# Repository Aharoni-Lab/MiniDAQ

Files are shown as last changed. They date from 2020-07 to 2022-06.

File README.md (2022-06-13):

# MiniDAQ
Simplified DAQ for Miniscopes and Minicams. This is effectively a smaller version of the [standard Miniscope DAQ](https://github.com/daharoni/Miniscope_DAQ_PCB) and does not include easily accessible trigger and sync connections but should support all other functionality of the Miniscope platform.

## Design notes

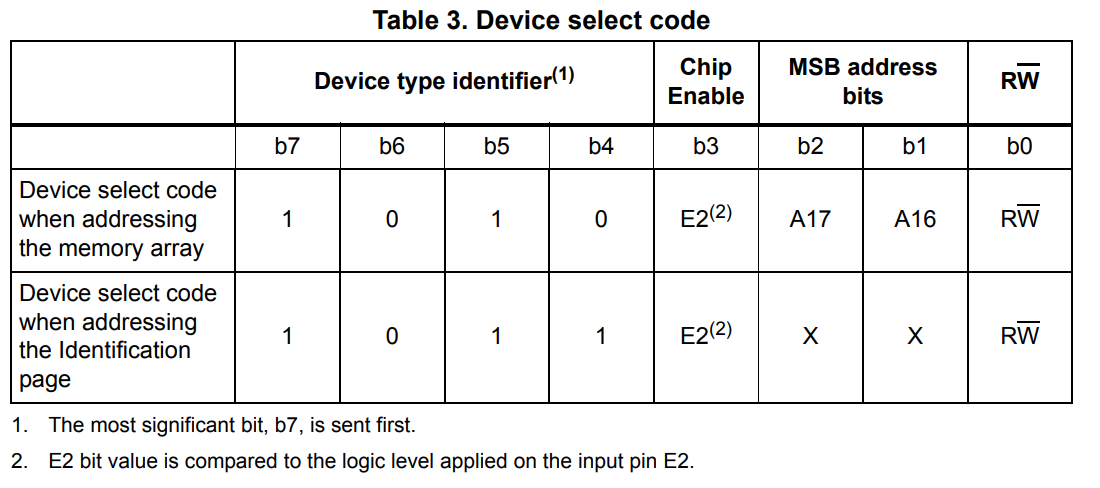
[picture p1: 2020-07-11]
KiCad/img/M24M02_I2C_ADDR.PNG

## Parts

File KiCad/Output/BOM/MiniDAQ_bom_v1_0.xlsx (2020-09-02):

Component | Description | Part | References | Value | Footprint | Quantity Per PCB | Datasheet | Part Number | Note | Size
1 | Unpolarized capacitor, small symbol | C_Small | C79 | 0 Res | C_0201_0603Metric_L | 1 | ~ | ERJ-1GN0R00C
2 | Unpolarized capacitor, small symbol | C_Small | C2 C5 C7 C10 C12 C15 C20 C23 C26 C30 C35 C37 C39 C40 C41 C43 C45 C46 C48 C50 C51 C53 C57 C58 C59 C61 C63 C65 C67 C68 C70 C72 C74 | 0.1uF | C_0201_0603Metric_L | 33 | ~ | CC0201KRX5R6BB104
3 | Unpolarized capacitor, small symbol | C_Small | C1 C6 C9 C13 C14 C18 C19 C24 C25 C29 C38 C42 C49 C54 C60 C64 C66 C69 C71 | 10nF | C_0201_0603Metric_L | 19 | ~ | CC0201KRX7R7BB103
4 | Unpolarized capacitor, small symbol | C_Small | C4 C22 C28 C32 C73 C75 | 10uF | C_0402_1005Metric_L | 6 | ~ | CC0402MRX5R5BB106
5 | Unpolarized capacitor, small symbol | C_Small | C55 C56 | 12pF | C_0201_0603Metric_L | 2 | ~ | CC0201JRNPO8BN120
6 | Unpolarized capacitor, small symbol | C_Small | C16 C21 C27 C31 C33 C34 C77 C78 | 1uF | C_0201_0603Metric_L | 8 | ~ | CC0201MRX5R5BB105
7 | Unpolarized capacitor, small symbol | C_Small | C36 C47 C52 | 2.2uF | C_0402_1005Metric_L | 3 | ~ | CC0402MRX5R6BB225
8 | Unpolarized capacitor, small symbol | C_Small | C44 C62 C76 | 22uF | C_0402_1005Metric_L | 3 | ~ | CL05A226MQ5N6J8
9 | Unpolarized capacitor, small symbol | C_Small | C3 C8 C11 | 4.7uF | C_0402_1005Metric_L | 3 | ~ | CC0402MRX5R6BB475
10 | Unpolarized capacitor, small symbol | C_Small | C17 | 47nF | C_0201_0603Metric_L | 1 | ~ | CC0201KRX5R5BB473
11 | Dual LED, cathodes on pins 3 and 4 | LTST-C155GEKT | D1 | LTST-C155GEKT | LED_4_P138_270X320X110L50X90N | 1 | https://media.digikey.com/pdf/Data%20Sheets/Lite-On%20PDFs/LTST-C155GEKT.pdf | LTST-C155GEKT
15 | USB 3.0 A connector | USB3_A | J1 | USB3_A | USB3_A_Plug_Wuerth_692112030100_Horizontal | 1 | ~ | 692112030100
16 | Edge mount SMA | SMA | J2 | SMA-J-P-H-ST-EM1 |  | 1 |  | SMA-J-P-H-ST-EM1
17 | FIXED IND 47UH 500MA 900 MOHM | ADL3225V-470MT-TL000 | L11 | ADL3225V-470MT-TL000 | L_1210_3225Metric_L | 1 | https://product.tdk.com/info/en/catalog/datasheets/inductor_automotive_decoupling_adl3225v_en.pdf | ADL3225V-470MT-TL000 | 47uH | 1210
18 | FERRITE BEAD 470 OHM 0603 1LN | BLM18PG471SN1D | L1 L2 L3 L5 L6 L8 L9 L10 | BLM18PG471SN1D | L_0603_1608Metric_L | 8 | https://www.murata.com/en-us/products/productdata/8796738650142/ENFA0003.pdf | BLM18PG471SN1D | 470 Ohms @ 100MHz | 603
19 | Inductor, small symbol | L_Small | L4 L7 | BLM21PG221SN1D | L_0805_2012Metric | 2 | https://www.murata.com/en-us/products/en-us/products/productdata/8796738977822/ENFA0005.pdf | BLM21PG221SN1D
20 | Inductor, small symbol | L_Small | L12 | LQM2HPN1R0MG0 | L_1008_2520Metric_L | 1 | https://www.mouser.com/datasheet/2/281/JELF243B-0019-1634195.pdf | LQM2HPN1R0MG0
21 | TRANS NPN 40V 0.2A DFN1006-3 | MMBT3904LP-7B | Q1 Q2 | MMBT3904LP-7B | TRXDFN3_101X61X53L25X15N | 2 | https://www.diodes.com/assets/Datasheets/ds31835.pdf | MMBT3904LP-7B
22 | Resistor, small US symbol | R_Small_US | R41 R42 | 0 | R_0201_0603Metric_ERJ_L | 2 | ~ | ERJ-1GN0R00C
23 | Resistor, small US symbol | R_Small_US | R5 R8 | 0 1% | R_0201_0603Metric_ERJ_L | 2 | ~ | ERJ-1GN0R00C
24 | Resistor, small US symbol | R_Small_US | R1 R2 R3 R9 R14 R15 R29 R43 | 10K | R_0201_0603Metric_ERJ_L | 8 | ~ | ERJ-1GNF1002C
25 | Resistor, small US symbol | R_Small_US | R4 R6 | 10K 1% | R_0201_0603Metric_ERJ_L | 2 | ~ | ERJ-1GNF1002C
26 | Resistor, small US symbol | R_Small_US | R12 | 200 1% | R_0201_0603Metric_ERJ_L | 1 | ~ | ERJ-1GEF2000C
27 | Resistor, small US symbol | R_Small_US | R16 R17 R18 R19 R20 R21 R22 R23 R26 R27 R28 R33 R34 R35 R36 R37 R38 R39 R40 | 22 | R_0201_0603Metric_ERJ_L | 19 | ~ | ERJ-1GNF22R0C
28 | Resistor, small US symbol | R_Small_US | R10 R11 R24 R25 R30 R31 R32 | 2k | R_0201_0603Metric_ERJ_L | 7 | ~ | ERJ-1GNF2001C
29 | Resistor, small US symbol | R_Small_US | R7 | 50 | R_0201_0603Metric_ERJ_L | 1 | ~ | ERJ-1GNF49R9C
30 | Resistor, small US symbol | R_Small_US | R13 | 6.04K 1% | R_0201_0603Metric_ERJ_L | 1 | ~ | ERJ-1GNF6041C
31 | EZ-USBÂ® FX3:SuperSpeed USB Controller | CYUSB3014 | U4 | CYUSB3014 | BGA121CP80_11X11_1000X1000X120B30 | 1 | https://www.cypress.com/file/140296/download | CYUSB3014-BZXC
32 | IC DESERIALIZER 12 BIT 48-VQFN | DS90UB934-Q1 | U1 | DS90UB934-Q1 | QFN_49_P50_700X700X100L40X24T410N | 1 | http://www.ti.com/lit/ds/symlink/ds90ub934-q1.pdf | DS90UB914ATRHSJQ1
33 | 2-Mbit serial IÂ²C bus EEPROM | M24M02-R | U5 | M24M02-R | M24M02-R | 1 | https://www.st.com/content/ccc/resource/technical/document/datasheet/b7/de/9b/f6/03/28/4e/8e/CD00290537.pdf/files/CD00290537.pdf/jcr:content/translations/en.C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 | M24M02-DRCS6TP/K
34 | USB Positive Overvoltage | NCP360 | U2 | NCP360 | SON7P65_200X200X55L30X30T160X90L | 1 | https://www.onsemi.com/pub/Collateral/NCP360-D.PDF | NCP360MUTBG
35 |  | NCP690MN50T2G(5V) | U7 | NCP692MN18T2G | NCP692MN50T2G | 1 | https://www.onsemi.com/pub/Collateral/NCP690-D.PDF | NCP692MN18T2G
36 | 2.5MHz, 1.5A Synchronous Step Down Regulator | SC189xULTRT | U6 | SC189CULTRT | SON_7P50_200X200X57L35X24T170X80N | 1 | https://www.mouser.com/datasheet/2/761/sc189-1366204.pdf | SC189CULTRT
37 | TVS Diode Array | SP3010-04UTG | U3 | SP3010-04UTG | uDFN-10 | 1 | https://www.littelfuse.com/~/media/electronics/datasheets/tvs_diode_arrays/littelfuse_tvs_diode_array_sp3010_datasheet.pdf.pdf | SP3010-04UTG
38 | 2.5mm x 2mm | SMD_CRYSTAL | Y1 | SMD_CRYSTAL | Crystal_SMD_2016-4Pin_2.0x1.6mm | 1 |  | CX2016DB19200H0FLJC2
Component Groups: | 38
Component Count: | 153
Fitted Components: | 153
Number of PCBs: | 1
Total components: | 153
Schematic Version: | v1.0
Schematic Date: | 2020-09-01
PCB Variant: | [u'default']
BoM Date: | 2020-07-15
Schematic Source: | C:\Users\DBAharoni\Documents\Projects\MiniDAQ\KiCad\MiniDAQ.sch
KiCad Version: | Eeschema (5.1.5)-3

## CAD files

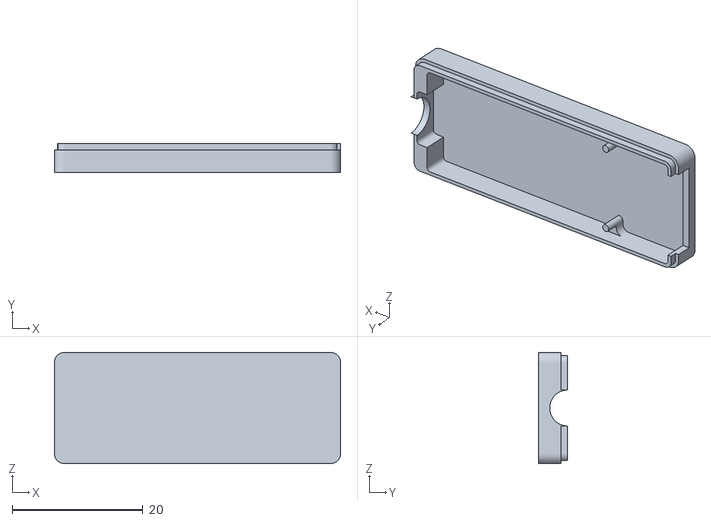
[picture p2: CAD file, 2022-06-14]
MiniDAQ-Body-Parts/MiniDAQ_Shell_Bottom.stl
43.8 x 4.50 x 17.0

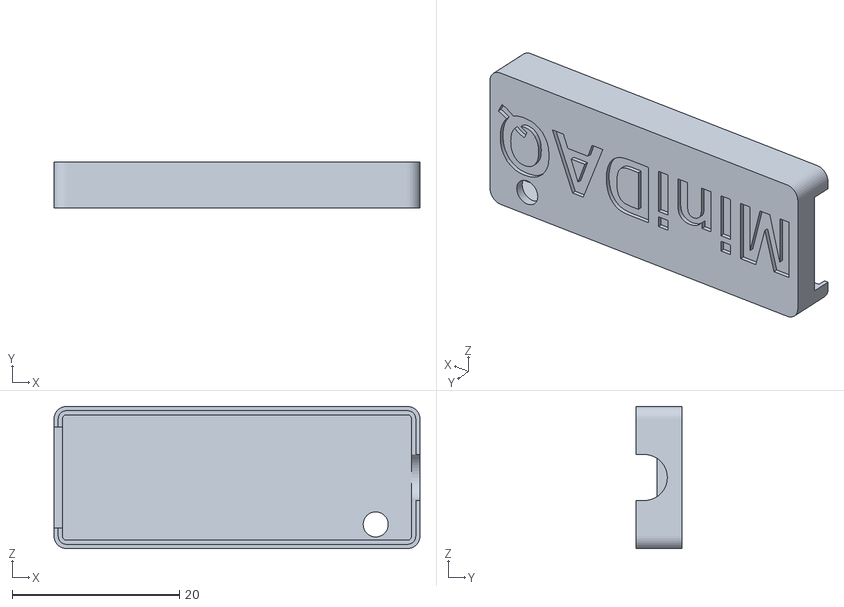
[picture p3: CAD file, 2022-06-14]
MiniDAQ-Body-Parts/MiniDAQ_Shell_Top.stl
43.8 x 5.50 x 17.0

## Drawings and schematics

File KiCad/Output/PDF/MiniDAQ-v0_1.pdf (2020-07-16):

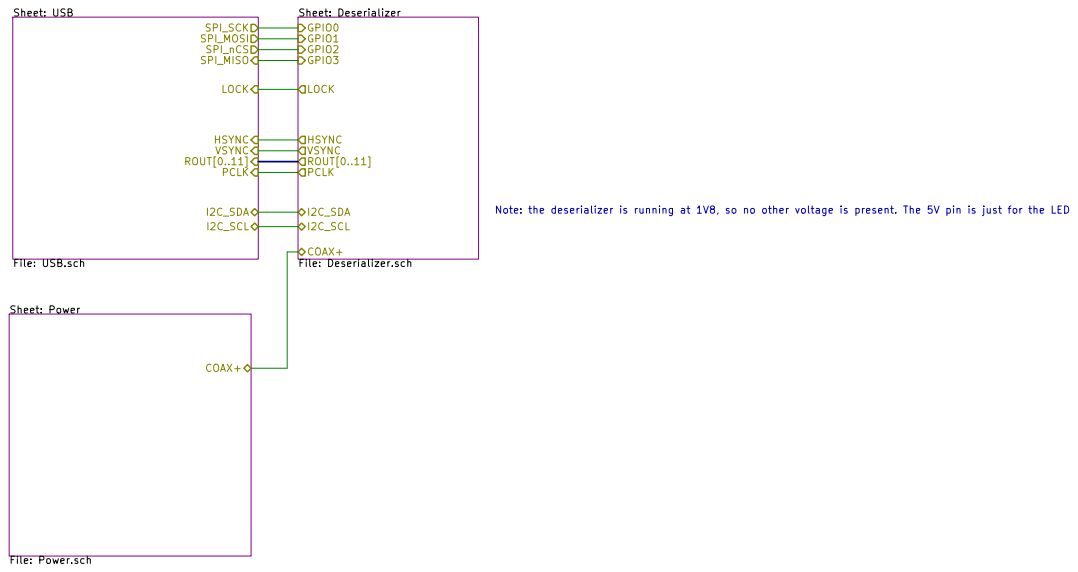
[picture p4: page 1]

File: MiniDAQ.sch Sheet: / Daniel Aharoni

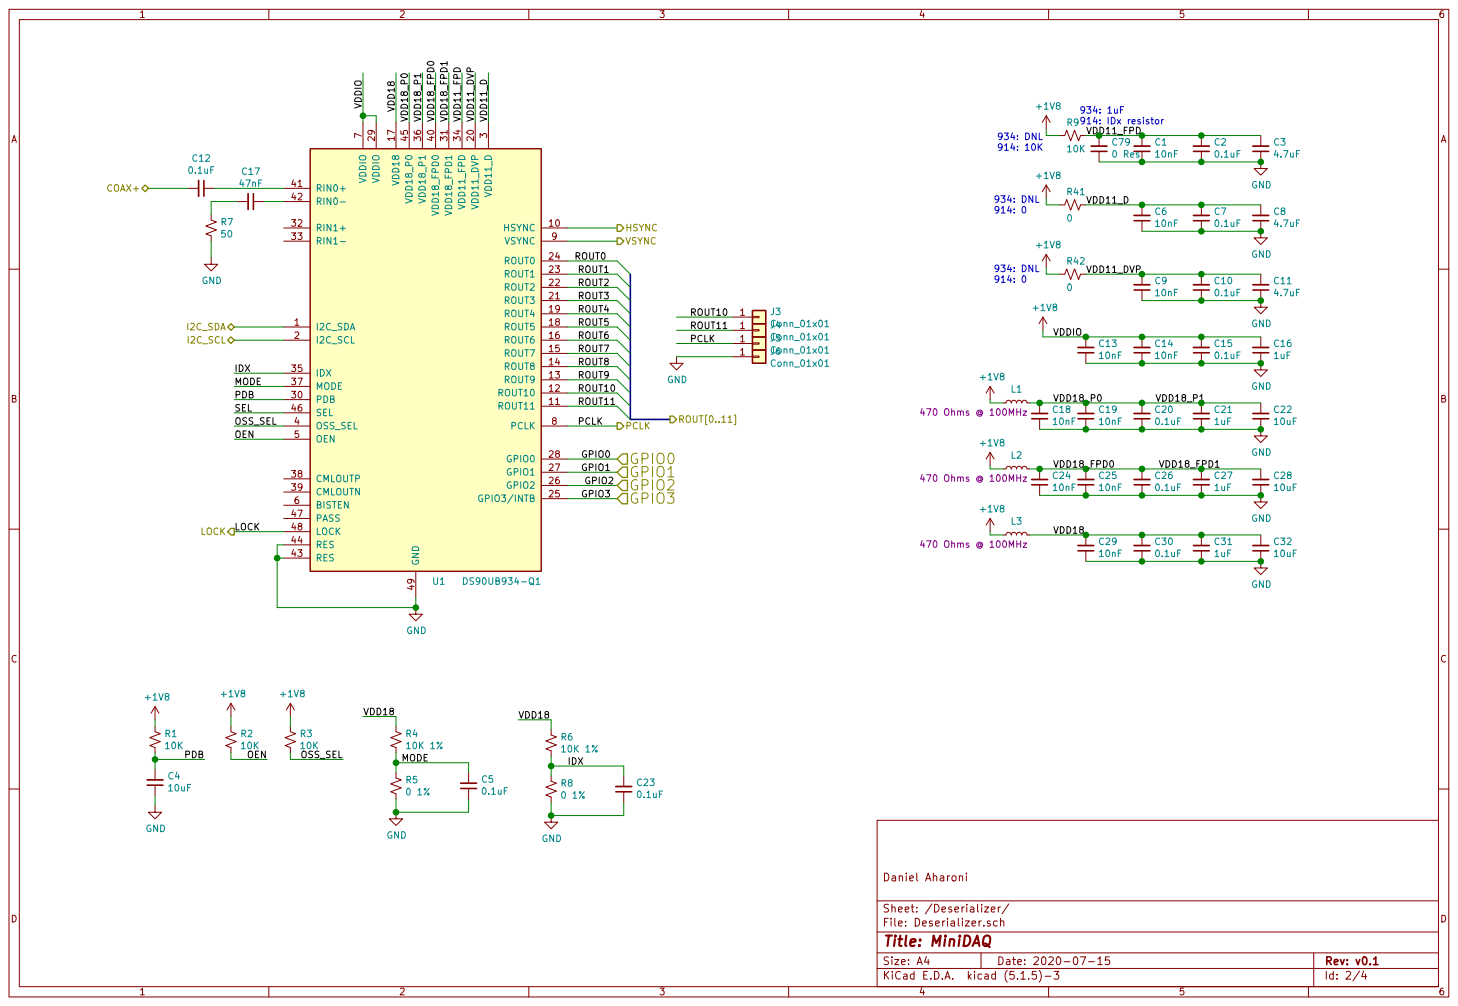
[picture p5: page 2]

File: Deserializer.sch Sheet: /Deserializer/ Daniel Aharoni GND

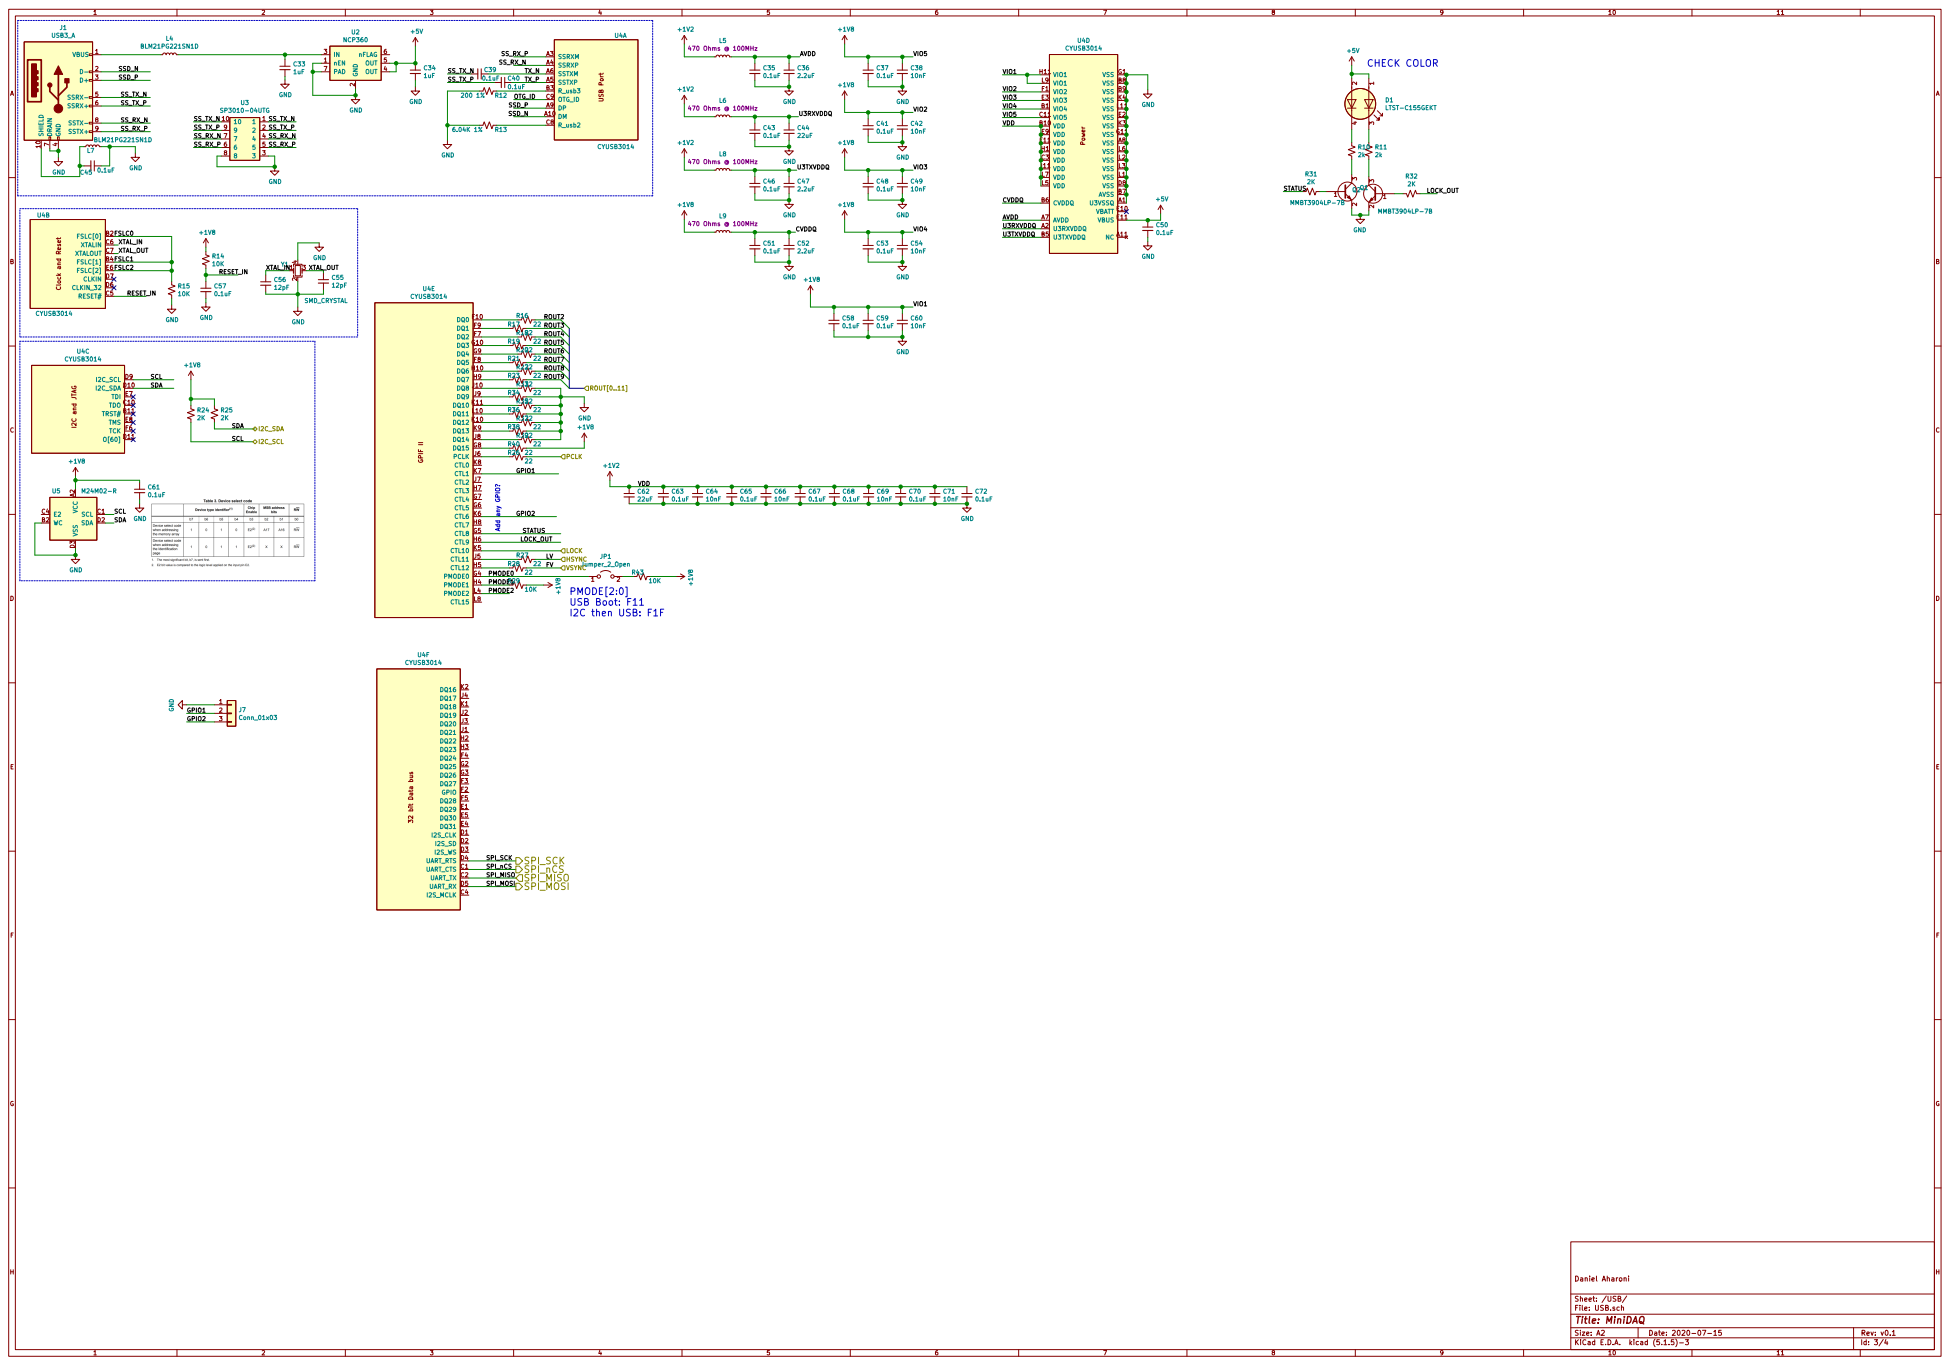
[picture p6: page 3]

File: USB.sch Sheet: /USB/ Daniel Aharoni

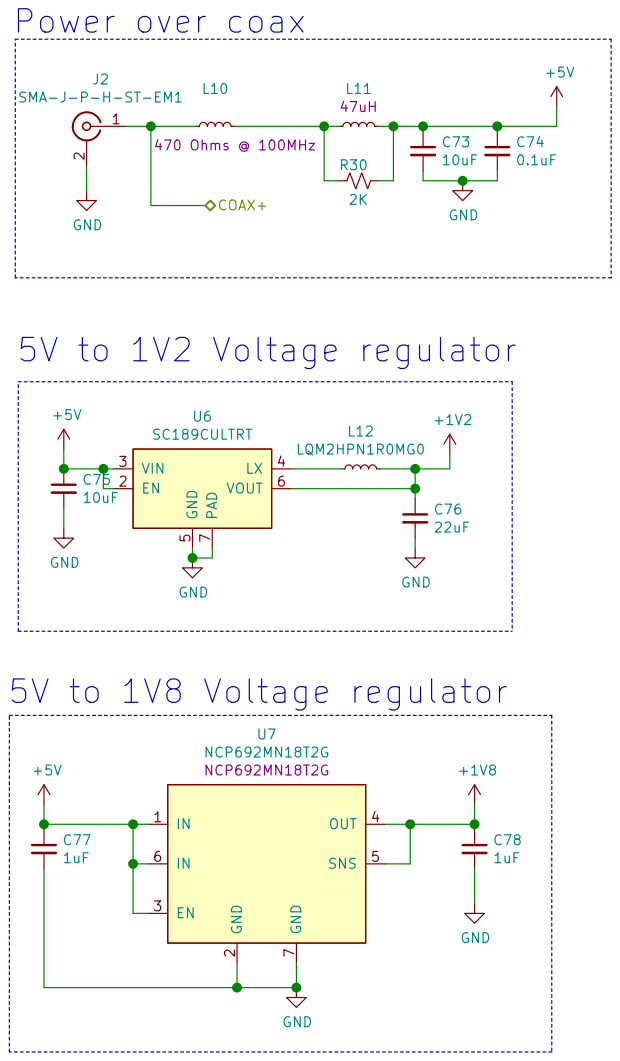
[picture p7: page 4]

2K COAX+ 5V to 1V8 Voltage regulator

File: Power.sch Sheet: /Power/ Daniel Aharoni

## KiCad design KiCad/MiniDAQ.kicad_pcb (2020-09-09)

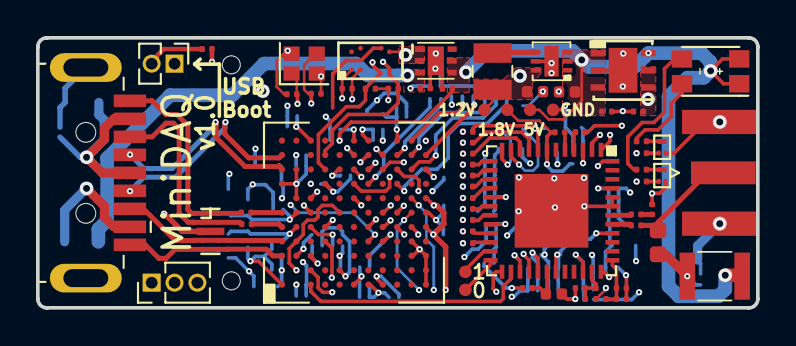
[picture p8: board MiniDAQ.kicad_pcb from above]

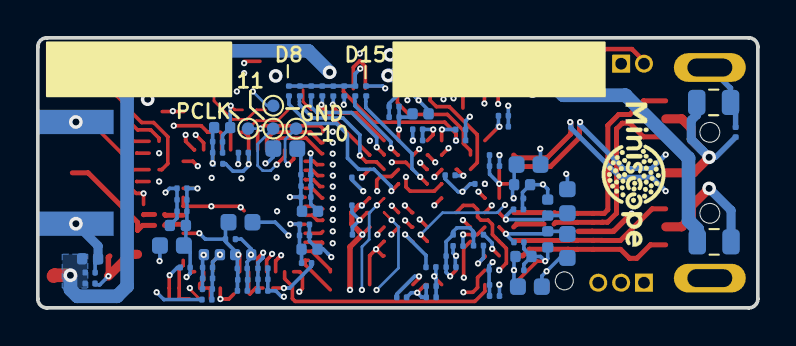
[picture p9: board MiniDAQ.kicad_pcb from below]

Board: 6 copper layers, 40.0 x 15.0 mm, 161 parts (93 on the bottom side), 96 nets.

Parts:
C1, C6, C9, C13, C14, C18, C19, C24, C25, C29, C38, C42, C49, C54, C60, C64, C66, C69, C71: 10nF; C_0201_0603Metric_L
C2, C5, C7, C10, C12, C15, C20, C23, C26, C30, C35, C37, C39, C40, C41, C43, C45, C46, C48, C50, C51, C53, C57, C58, C59, C61, C63, C65, C67, C68, C70, C72, C74: 0.1uF; C_0201_0603Metric_L
C3, C8, C11: 4.7uF; C_0402_1005Metric_L
C4, C22, C28, C32, C73, C75: 10uF; C_0402_1005Metric_L
C16, C21, C27, C31, C33, C34, C77, C78: 1uF; C_0201_0603Metric_L
C17: 47nF; C_0201_0603Metric_L
C36, C47, C52: 2.2uF; C_0402_1005Metric_L
C44, C62, C76: 22uF; C_0402_1005Metric_L
C55, C56: 12pF; C_0201_0603Metric_L
C79: 0 Res; C_0201_0603Metric_L
D1: LTST-C155GEKT; LED_4_P138_270X320X110L50X90N
J1: USB3_A; USB3_A_Plug_Wuerth_692112030100_Horizontal
J2: SMA-J-P-H-ST-EM1; SMA_Samtec_SMA-J-P-H-ST-EM1_EdgeMount
J3, J4, J5, J6: Conn_01x01; Conn_1x1_700_Circular_Pad
J7: Conn_01x03; PinHeader_1x03_P1.27mm_Vertical
JP1: Jumper_2_Open; PinHeader_1x02_P1.27mm_Vertical
J_NA: Conn_01x01; Conn_1x1_700_Circular_Pad
J_NA#2, J_NA#3, J_NA#4, J_NA#5, J_NA#6, J_NA#7, J_NA#8: Conn_01x01; Conn_1x1_700_Circular_Pad
L1, L2, L3, L5, L6, L8, L9, L10: BLM18PG471SN1D; L_0603_1608Metric_L
L4, L7: BLM21PG221SN1D; L_0805_2012Metric
L11: ADL3225V-470MT-TL000; L_1210_3225Metric_L
L12: LQM2HPN1R0MG0; L_1008_2520Metric_L
Q1, Q2: MMBT3904LP-7B; TRXDFN3_101X61X53L25X15N
R1, R2, R3, R9, R14, R15, R29, R43: 10K; R_0201_0603Metric_ERJ_L
R4, R6: 10K 1%; R_0201_0603Metric_ERJ_L
R5, R8: 0 1%; R_0201_0603Metric_ERJ_L
R7: 50; R_0201_0603Metric_ERJ_L
R10, R11: 2k; R_0201_0603Metric_ERJ_L
R12: 200 1%; R_0201_0603Metric_ERJ_L
R13: 6.04K 1%; R_0201_0603Metric_ERJ_L
R16, R17, R18, R19, R20, R21, R22, R23, R26, R27, R28, R33, R34, R35, R36, R37, R38, R39, R40: 22; R_0201_0603Metric_ERJ_L
R24, R25, R30, R31, R32: 2K; R_0201_0603Metric_ERJ_L
R41, R42: 0; R_0201_0603Metric_ERJ_L
U1: DS90UB934-Q1; QFN_49_P50_700X700X100L40X24T410N
U2: NCP360; SON7P65_200X200X55L30X30T160X90L
U3: SP3010-04UTG; uDFN-10
U4: CYUSB3014; BGA121CP80_11X11_1000X1000X120B30
U5: M24M02-R
U6: SC189CULTRT; SON_7P50_200X200X57L35X24T170X80N
U7: NCP692MN18T2G; NCP692MN50T2G
Y1: SMD_CRYSTAL; Crystal_SMD_2016-4Pin_2.0x1.6mm

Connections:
+1V2: C62.1, C63.1, C64.1, C65.1, C66.1, C67.1, C68.1, C69.1, C70.1, C71.1, C72.1, C76.1, J_NA#6.1, L5.1, L6.1, L8.1, L12.2, U4.B10, U4.C3, U4.E9, U4.F11, U4.H1, U4.J11, U4.L5, U4.L7, U6.6
+1V8: C13.2, C14.2, C15.2, C16.2, C37.1, C38.1, C41.1, C42.1, C48.1, C49.1, C53.1, C54.1, C58.1, C59.1, C60.1, C61.1, C78.1, J_NA#5.1, L1.1, L2.1, L3.1, L9.1, R1.1, R2.1, R3.1, R9.2, R14.1, R24.1, R25.1, R29.1, R40.1, R41.2, R42.2, R43.1, U1.7, U1.29, U4.B1, U4.C11, U4.E3, U4.F1, U4.H11, U4.L9, U5.A2, U7.4, U7.5
+5V: C34.1, C50.1, C73.1, C74.1, C75.1, C77.1, D1.1, D1.2, J_NA#3.1, L11.2, R30.2, U2.4, U2.5, U4.E11, U6.2, U6.3, U7.1, U7.3, U7.6
/Deserializer/COAX+: C12.2, J2.1, L10.1
/Deserializer/GPIO0: U1.28, U4.D4
/Deserializer/GPIO1: U1.27, U4.D5
/Deserializer/GPIO2: U1.26, U4.C1
/Deserializer/GPIO3: U1.25, U4.C2
/Deserializer/HSYNC: R27.1, U1.10
/Deserializer/I2C_SCL: R24.2, U1.2, U4.D9, U5.C1
/Deserializer/I2C_SDA: R25.2, U1.1, U4.D10, U5.D2
/Deserializer/IDX: C23.2, R6.2, R8.1, U1.35
/Deserializer/LOCK: U1.48, U4.K5
/Deserializer/MODE: C5.2, R4.2, R5.1, U1.37
/Deserializer/OEN: R2.2, U1.5
/Deserializer/OSS_SEL: R3.2, U1.4
/Deserializer/PCLK: J5.1, R26.1, U1.8
/Deserializer/PDB: C4.2, R1.2, U1.30
/Deserializer/ROUT0: J_NA#7.1, U1.24
/Deserializer/ROUT1: J_NA#8.1, U1.23
/Deserializer/ROUT2: R16.1, U1.22
/Deserializer/ROUT3: R17.1, U1.21
/Deserializer/ROUT4: R18.1, U1.19
/Deserializer/ROUT5: R19.1, U1.18
/Deserializer/ROUT6: R20.1, U1.16
/Deserializer/ROUT7: R21.1, U1.15
/Deserializer/ROUT8: R22.1, U1.14
/Deserializer/ROUT9: R23.1, U1.13
/Deserializer/ROUT10: J3.1, U1.12
/Deserializer/ROUT11: J4.1, U1.11
/Deserializer/VDD11_D: C6.2, C7.2, C8.2, R41.1, U1.3
/Deserializer/VDD11_DVP: C9.2, C10.2, C11.2, R42.1, U1.20
/Deserializer/VDD11_FPD: C1.2, C2.2, C3.2, C79.2, R9.1, U1.34
/Deserializer/VDD18: C29.2, C30.2, C31.2, C32.2, L3.2, R4.1, R6.1, U1.17
/Deserializer/VDD18_FPD0: C24.2, C25.2, C26.2, C27.2, C28.2, L2.2, U1.31, U1.40
/Deserializer/VDD18_P0: C18.2, C19.2, C20.2, C21.2, C22.2, L1.2, U1.36, U1.45
/Deserializer/VSYNC: R28.1, U1.9
/USB/AVDD: C35.1, C36.1, L5.2, U4.A7
/USB/CVDDQ: C51.1, C52.1, L9.2, U4.B6
/USB/FSLC0: R15.1, U4.B2, U4.B4, U4.E6
/USB/GPIO1: J7.2, U4.K7
/USB/GPIO2: J7.3, U4.K6
/USB/LOCK_OUT: R32.2, U4.H6
/USB/PMODE0: JP1.1, U4.G4
/USB/PMODE1: R29.2, U4.H4
/USB/RESET_IN: C57.1, R14.2, U4.C5
/USB/SSD_N: J1.2, U4.A10
/USB/SSD_P: J1.3, U4.A9
/USB/SS_RX_N: J1.8, U3.4, U3.7, U4.A4
/USB/SS_RX_P: J1.9, U3.5, U3.6, U4.A3
/USB/SS_TX_N: C39.2, J1.5, U3.1, U3.10
/USB/SS_TX_P: C40.2, J1.6, U3.2, U3.9
/USB/STATUS: R31.2, U4.G5
/USB/TX_N: C39.1, U4.A6
/USB/TX_P: C40.1, U4.A5
/USB/U3RXVDDQ: C43.1, C44.1, L6.2, U4.A2
/USB/U3TXVDDQ: C46.1, C47.1, L8.2, U4.B5
/USB/XTAL_IN: C56.1, U4.C6, Y1.1
/USB/XTAL_OUT: C55.1, U4.C7, Y1.3
GND: C1.1, C2.1, C3.1, C4.1, C5.1, C6.1, C7.1, C8.1, C9.1, C10.1, C11.1, C13.1, C14.1, C15.1, C16.1, C18.1, C19.1, C20.1, C21.1, C22.1, C23.1, C24.1, C25.1, C26.1, C27.1, C28.1, C29.1, C30.1, C31.1, C32.1, C33.2, C34.2, C35.2, C36.2, C37.2, C38.2, C41.2, C42.2, C43.2, C44.2, C45.1, C46.2, C47.2, C48.2, C49.2, C50.2, C51.2, C52.2, C53.2, C54.2, C55.2, C56.2, C57.2, C58.2, C59.2, C60.2, C61.2, C62.2, C63.2, C64.2, C65.2, C66.2, C67.2, C68.2, C69.2, C70.2, C71.2, C72.2, C73.2, C74.2, C75.2, C76.2, C77.2, C78.2, C79.1, J1.4, J1.7, J2.2, J6.1, J7.1, J_NA#4.1, L7.2, Q1.2, Q2.2, R5.2, R7.2, R8.2, R12.2, R13.2, R15.2, R33.1, R34.1, R35.1, R36.1, R37.1, R38.1, R39.1, U1.43, U1.44, U1.49, U2.1, U2.2, U2.7, U3.3, U3.8, U4.A1, U4.A8, U4.B7, U4.B8, U4.B9, U4.D8, U4.E2, U4.G1, U4.G11, U4.K3, U4.K4, U4.L1, U4.L2, U4.L3, U4.L6, U4.L11, U5.B2, U5.D3, U6.5, U6.7, U7.2, U7.7, Y1.2, Y1.4
unnamed: C12.1, U1.41
unnamed: C17.1, U1.42
unnamed: C17.2, R7.1
unnamed: C33.1, L4.2, U2.3
unnamed: C45.2, J1.10, L7.1
unnamed: D1.3, R11.1
unnamed: D1.4, R10.1
unnamed: J1.1, L4.1
unnamed: JP1.2, R43.2
unnamed: L10.2, L11.1, R30.1
unnamed: L12.1, U6.4
unnamed: Q1.1, R31.1
unnamed: Q1.3, R10.2
unnamed: Q2.1, R32.1
unnamed: Q2.3, R11.2
unnamed: R12.1, U4.B3
unnamed: R13.1, U4.C8
unnamed: R16.2, U4.F10
unnamed: R17.2, U4.F9
unnamed: R18.2, U4.F7
unnamed: R19.2, U4.G10
unnamed: R20.2, U4.G9
unnamed: R21.2, U4.F8
unnamed: R22.2, U4.H10
unnamed: R23.2, U4.H9
unnamed: R26.2, U4.J6
unnamed: R27.2, U4.J5
unnamed: R28.2, U4.H5
unnamed: R33.2, U4.J10
unnamed: R34.2, U4.J9
unnamed: R35.2, U4.K11
unnamed: R36.2, U4.L10
unnamed: R37.2, U4.K10
unnamed: R38.2, U4.K9
unnamed: R39.2, U4.J8
unnamed: R40.2, U4.G8

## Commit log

2020-07-10 Create KiCad project for MiniDAQ
    [MiniDAQ.kicad_pcb, MiniDAQ.sch]
2020-07-11 Add initial schematic layout and some initial components
    [Deserializer.sch, Power.sch, USB.sch]
2020-07-11 Layout initial schematic of deserializer
    [Deserializer.sch, USB.sch]
2020-07-12 Layout schematic for the most part. Needs to be fully reviewed.
    [Deserializer.sch, Power.sch, USB.sch]
2020-07-13 1.8 Voltage regulator added, minor fixes to the schematic
    - Added the NCP690MN18T2G 5V to 1.8 Volt voltage regulator
    - Checked the connections in the PCB
    - Added annotation on the deserializer output
    [Power.sch, USB.sch]
2020-07-13 Update 1.8V LDO and change USB3 micro-B connector
    [MiniDAQ.sch, Power.sch, USB.sch]
2020-07-13 Hierarchical power pins added
    - Added the 1V8, 1V2 and 5V pins to connect the sheets one to each other
    - Slightly modified the main sheet to make the connections clear
    [Deserializer.sch, MiniDAQ.sch, Power.sch, USB.sch]
2020-07-13 Remove global power sheet labels. Switch USB connector to type A
    [Deserializer.sch, MiniDAQ.sch, Power.sch, USB.sch]
2020-07-13 Annotate all components.
    [Deserializer.sch, Power.sch, USB.sch]
2020-07-13 Update footprint of all components and switch many to 0201s
    [Deserializer.sch, Power.sch, USB.sch]
2020-07-14 Update footprints and add 3D models to all comoponents. Ready for layout + routing.
    [MiniDAQ.kicad_pcb, Power.sch, USB.sch]
2020-07-14 Correct USB to CYUSB3014 connections. I HOPE THIS IS CORRECT!
    [MiniDAQ.kicad_pcb, USB.sch]
2020-07-15 Route PCB. 1.2V and final 5V connection left. Then adding headers
    [Deserializer.sch, MiniDAQ.kicad_pcb, MiniDAQ.sch, Power.sch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]
2020-07-16 All files for v0.1 fab and assembly through PCBway
    [Deserializer.sch, MiniDAQ-B_Cu.gbr, MiniDAQ-B_Mask.gbr, MiniDAQ-B_Paste.gbr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]
2020-09-02 Minor changes and added test pads for possible v1.0 of MiniDAQ
    [MiniDAQ-B_Cu.gbr, MiniDAQ-B_Mask.gbr, MiniDAQ-B_Paste.gbr, MiniDAQ-B_SilkS.gbr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]
2020-09-02 Update rev on schematic sheets.
    [Deserializer.sch, MiniDAQ.kicad_pcb, MiniDAQ.sch, Power.sch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]
2020-09-09 Update v1.0 gerbers and generate .step file.
    [MiniDAQ-B_Cu.gbr, MiniDAQ-B_Mask.gbr, MiniDAQ-B_Paste.gbr, MiniDAQ-B_SilkS.gbr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]
2022-06-14 Addes Body Parts
    - Added STL files for the bottom and top shell
    [MiniDAQ_Shell_Bottom.stl, MiniDAQ_Shell_Top.stl]

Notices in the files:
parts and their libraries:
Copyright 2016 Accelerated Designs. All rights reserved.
